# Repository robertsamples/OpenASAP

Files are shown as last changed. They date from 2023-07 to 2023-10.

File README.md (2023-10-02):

# OpenASAP
An Open Source 3D printed Atmospheric Solids Analysis Probe


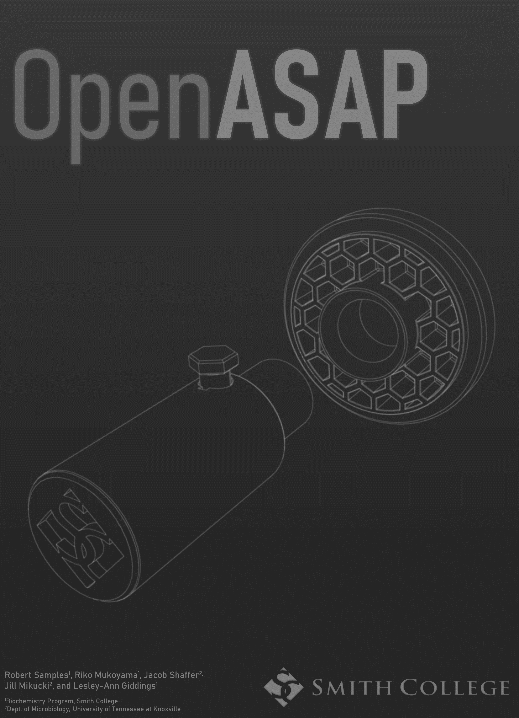
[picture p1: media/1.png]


## Video Tutorial

Click the preview to view the video tutorial and demonstration

[](https://www.youtube.com/watch?v=MM99iZ1kHVs "OpenASAP Tutorial")

## Material selection
### Resin
Any MSLA or SLA resin intended for high temperature applications can be used according to the manufacturer’s instructions. Sirayatech Sculpt Ultra and Formlabs resins have been verified to work. The probe body should be printed in the upright orientation due to the design of the internal structure.

### FDM
An FDM printer may be used with a material with an appropriately high heat deflection temperature such as nylon, polycarbonate, or annealed PLA according to the manufacturer’s instructions. ABS should not be used as depolymerization and release of styrene may cause high MS background, although this has not been proven. Annealed carbon fiber PLA is suggested as the preffered material as it has been proven to withstand the temperatures of the MS inlet for long periods of time, does not release volatile organic compounds in our experience, and is easy to print with an affordable hardened steel nozzle on an unenclosed printer. We suggest use of a 0.4 mm nozzle with standard voron settings (3-4 perimeters, 40% infill) and organic/tree supports inside the button channel.

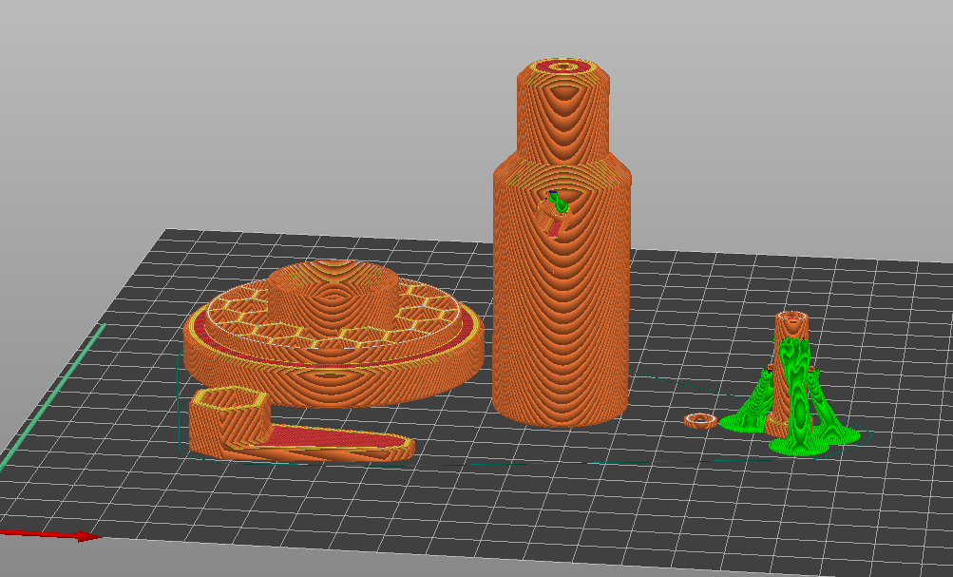
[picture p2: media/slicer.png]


If carbon fiber PLA is selected part annealing may be done in a laboratory oven, however we annealed parts using the printer heat bed. This was done by placing the parts on a 1 cm bed of gyroid infill printed with 3 walls and no top layers to allow airflow, covering the parts with a box made of 1 cm packing foam in which the 3D printer was shipped, and heating the bed to 100 °C for 30 minutes. Parts were allowed to cool slowly to below the glass transition temperature of approximately 50 °C before being removed from the chamber. Corrections for any contraction and expansion of printed parts were done by printing a 20 mm calibration cube and measuring the X, Y, and Z dimensions before and after annealing. A 1% contraction in X and Y dimensions and 2% expansion in Z dimension were found and thus parts were scaled prior to slicing to compensate for these modifications. Scaling requirements may differ depending on material selection and printing parameters.

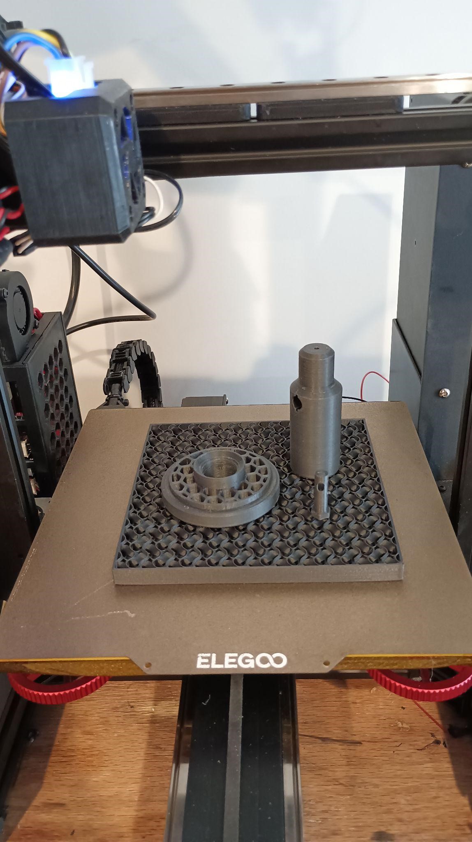
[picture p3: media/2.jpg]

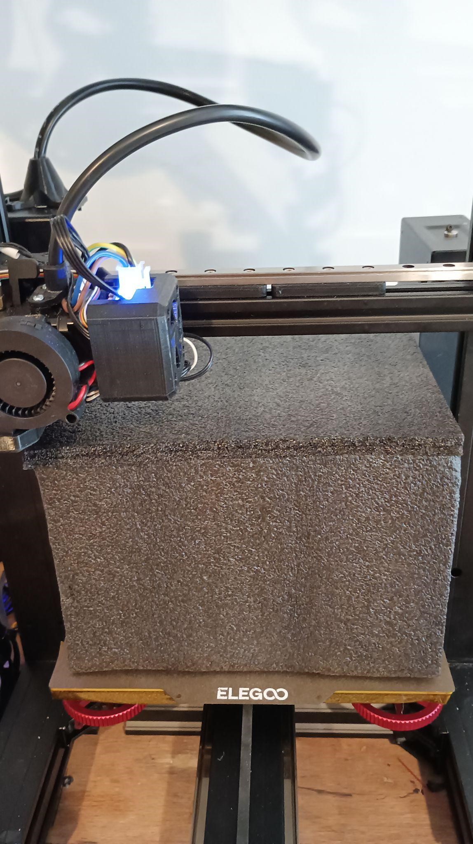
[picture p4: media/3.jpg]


## Postprocessing and assembly

Remove support material if applicable, removal of supports from the inside of the probe channel carefully using forceps or dental picks. Anneal if using carbon fiber PLA, Verify parts fit together properly by inserting the button into the button hole and use the wrench to ensure the button can be turned ¼ turn clockwise to align guide cylinders on the side of the button with the travel channel. Remove the button afterwards

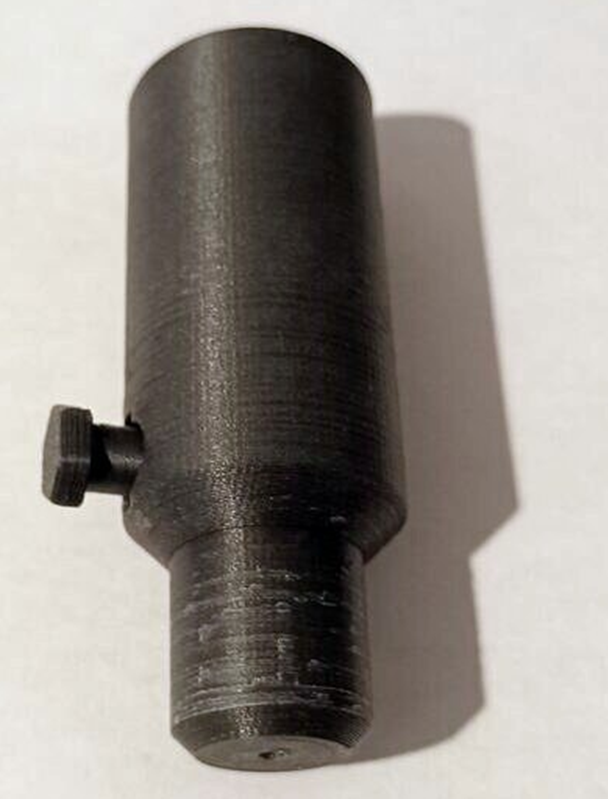
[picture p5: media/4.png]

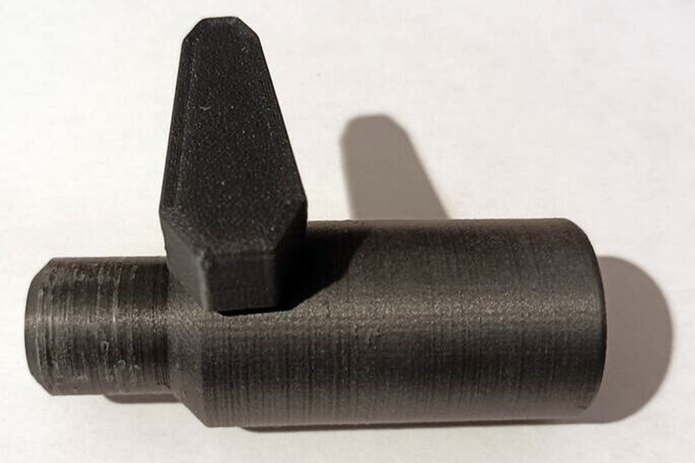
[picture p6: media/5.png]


Disassemble a retractable ballpoint pen or obtain a 4.25 x 18 mm or similar compression spring. The spring shown we used was obtained from a PaperMate InkJoy 300RT pen. The exact dimensions are not critical provided the probe button can reach the depth required to turn into the travel channel. A spring that is longer may be cut to length.

Confirm the spring length, which allows the probe button to be locked into the travel channel. To do this, the spring is placed in the recess of the button and the spring spacer is placed around the spring to prevent it from bending in the button hole. The button is reinserted into the probe as before. If it does not bottom out and turn, try a different pen, or cut the spring to length. Complete the final reassembly of the probe. Although not required,we suggest using a drop of cyanoacrylate glue around the spring spacer and recess in the probe button to secure these to the spring.

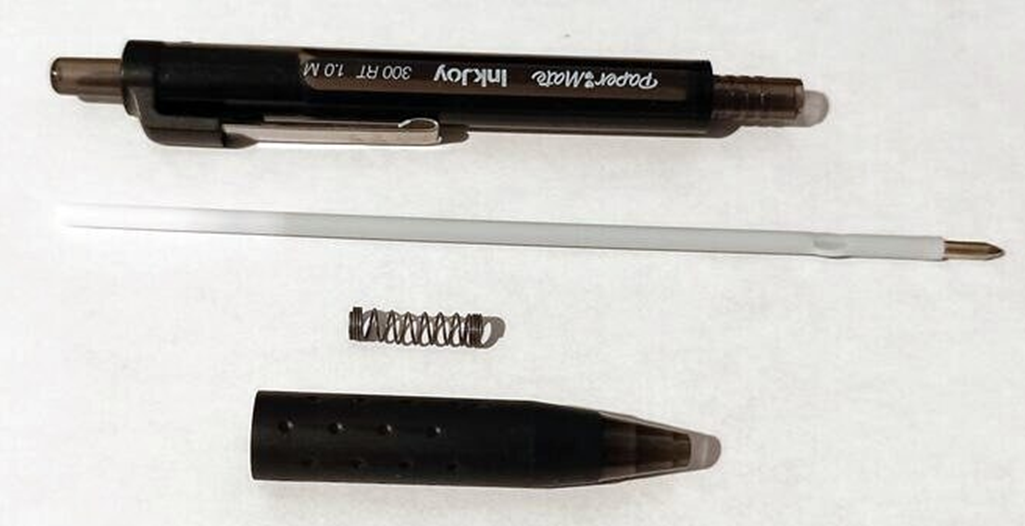
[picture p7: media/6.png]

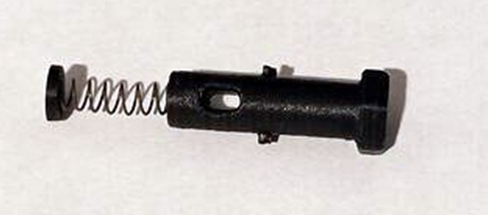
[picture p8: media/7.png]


## Installation

Unscrew the four M2 screws securing the outer housing plate screws on the left side and top of the source housing, as well as the x alignment adjustment nut.



Remove the M4 socket cap screw securing the source housing window side flange.



Remove the flange and replace the acrylic window with printed port, then reassemble flange and housing plates.




Install the IonMax source onto the MS interface and confirm that the tip of the capillary aligns with the MS inlet.


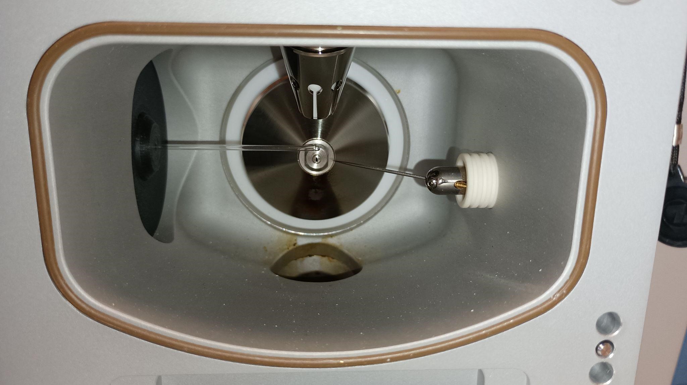
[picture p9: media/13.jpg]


## Use

### Safety
When operating the openASAP system, it is important to avoid contact with heated or electrically charged source components as they can reach high voltages and temperatures. We recommend always putting the mass spectrometer in standby mode when handling the source. Additionally, an electrically insulating material, such as glass, should be used for the sample collecting component of the probe.

### Instrument Configuration
Before using the openASAP system, the APCI source and corona discharge needle must be properly installed in the mass spectrometer housing following the manufacturer's instructions. For Thermo instruments, this involves inserting the APCI source and connecting the LEMO electrical connectors and fittings for auxiliary and sheath gas flow. The corona discharge needle should be inserted into the needle hole and the needle grub screw tightened to secure it. High voltage is supplied through a coaxial LEMO connection on the top of the source housing.

The APCI settings may need to be adjusted based on the analyte and instrument being used. For Thermo instruments, we recommend using the following settings as a starting point: Probe position C, a heater temperature of 325 °C, 5 μA current, and a sheath and auxiliary gas flow rate of 30 and 10 arbitrary units, respectively.

### Sampling

Watch the video (https://github.com/robertsamples/OpenASAP/assets/64489385/52e8197a-4d4a-41fe-b455-a457a1216c5c)

_Video of a 30 second acquisition with a previous vesion of the OpenASAP probe_

To load a capillary into the ASAP probe, depress the button and insert the capillary open end first until it reaches the maximum depth.

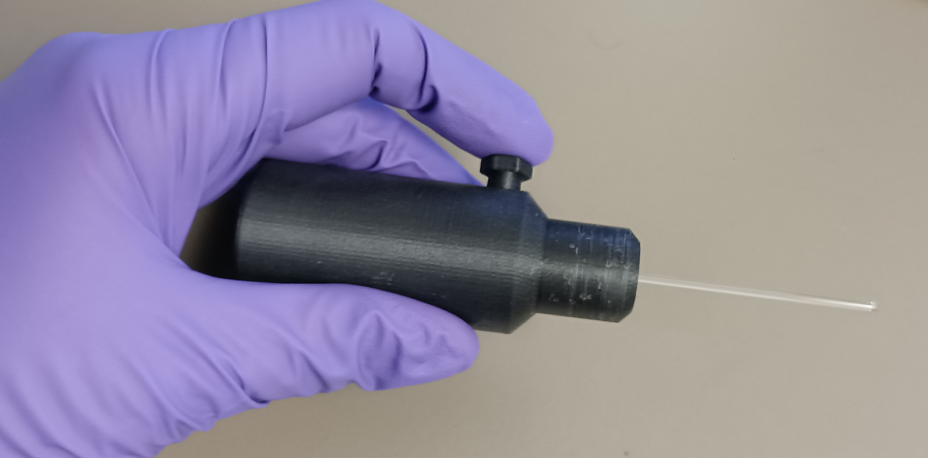
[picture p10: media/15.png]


 Collect the sample on the probe tip and then insert it into the APCI source after starting a continuous or set duration acquisition. 

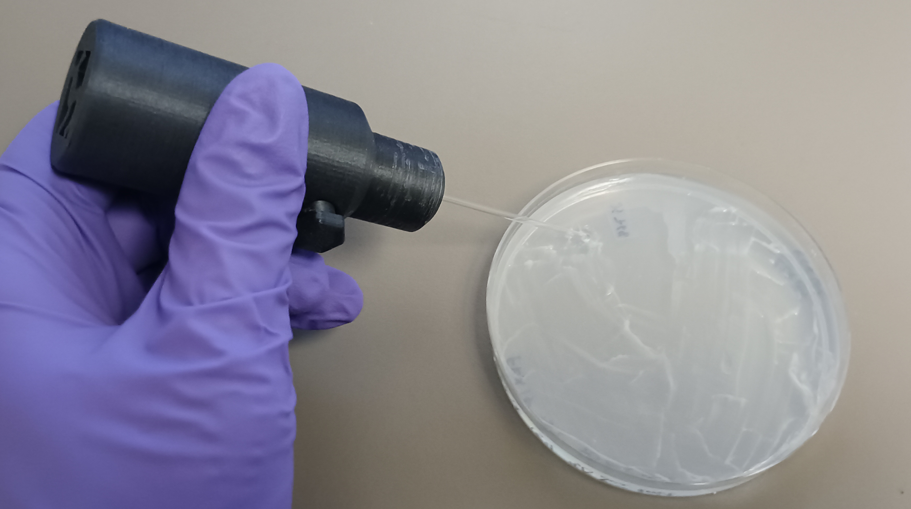
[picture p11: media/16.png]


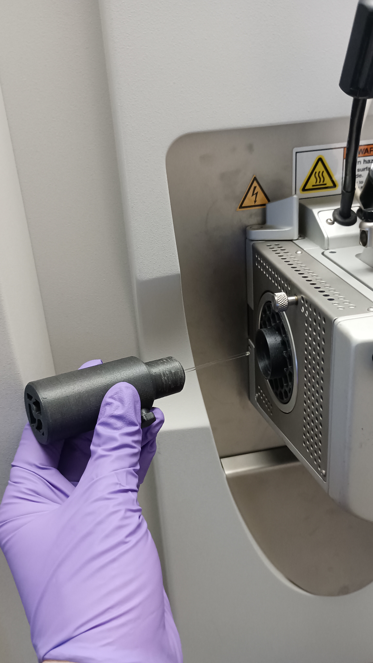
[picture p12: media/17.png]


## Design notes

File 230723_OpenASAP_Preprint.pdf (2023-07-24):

Article title
OpenASAP: an Affordable 3D Printed Atmospheric Solids Analysis Probe (ASAP) Mass Spectrometry System for Direct Analysis of Solid and Liquid Samples

Authors
Robert Samples¹*, Riko Mukoyama¹

, Jacob Shaffer²

, Jill Mikucki²

, and Lesley-Ann Giddings¹ Affiliations

### 1. Biochemistry Program, Smith College, 100 Green St Northampton, MA 01063 2. Department of Microbiology, University of Tennessee at Knoxville, Knoxville, TN 37902

Corresponding author’s email address and Twitter handle
rsamples@smith.edu. @RobertMSamples

### Abstract

Atmospheric Solids Analysis Probe (ASAP) mass spectrometry is a versatile technique allowing direct sampling of solid and liquid samples, but its adoption is limited due to the high cost of commercial ASAP systems. To address this, we present OpenASAP, an open-source ASAP system for mass spectrometers that can be fabricated for under $20 using 3D printing. Our design is readily adaptable to instruments from different manufacturers and can be produced with a variety of additive manufacturing techniques on consumer-grade 3D printers. The probe allows for rapid sampling of solid and liquid samples without sample preparation, making it useful for high throughput screening, investigating spatial localization and function of analytes in biological samples, and incorporating mass spectrometry in teaching. We demonstrate its effectiveness by obtaining mass spectra of three natural product standards at levels as low as 10 ng/ml in liquid samples, and detecting these metabolites in microbial cultures that are difficult to analyze due to complex sample matrices or analyte properties. Furthermore, we demonstrate direct sampling of thin layer chromatography (TLC) spots of these cultures.

### Keywords

Mass Spectrometry, Atmospheric Solids Analysis Probe, Ambient Ionization

### Specifications table

Hardware name | OpenASAP
Subject area | ● Chemistry and biochemistry ● Biological sciences (e.g., microbiology and biochemistry) ● Environmental, planetary and agricultural sciences ● Educational tools and open source alternatives to existing infrastructure
Hardware type | ● Measuring physical properties and in-lab sensors ● Biological sample handling and preparation
Closest commercial analog | Waters ASAP Probe IonSense ASAP System Advion ASAP System

Open source license | GNU General Public License (GPL)
Cost of hardware | $2.50-12.50
Source file repository | http://doi.org/10.5281/zenodo.8173130
OSHWA certification UID | Pending review

### 1. Hardware in context

Mass Spectrometry (MS) has proven to be an indispensable tool in analysis of complex mixtures and trace analytes in the biological and chemical sciences. [1] However, the most commonly used methods of introducing analytes into the mass spectrometer, including gas chromatography (GC-MS), liquid chromatography (LC-MS), and direct injection require time consuming liquid sample preparation. [2] These methods can also introduce nonvolatile salts and detergents that may interfere with sample analysis[3] or be deposited in a gas chromatography column or mass spectrometer. [4] These limitations reduce the utility of MS in situations where rapid sampling of crude materials is desired.

To overcome these limitations, several atmospheric ionization techniques have been developed with varying ranges of applications, analyte coverage, sample preparation requirements, and cost. [5] These ambient ionization methods involve direct sampling and ionization of analytes. [5] One of the simplest atmospheric ionization techniques is the Atmospheric Solids Analysis Probe (ASAP), [6] which is a peripheral device used in MS to allow rapid probe-based sampling of solids and liquids in conjunction with an Atmospheric Pressure Chemical Ionization (APCI) source. ASAP probes typically consist of a handle into which a thermostable and electrically insulating single-use sampling capillary can be inserted.
[7] A small quantity of solid or liquid sample can be collected on the surface of the capillary, which can be inserted into a port in the mass spectrometer source housing that positions the capillary between the mass spectrometer inlet and the APCI source. The position of the capillary enables analytes to be volatilized and ionized by the heated nitrogen plasma emitted by the APCI source. ASAP-MS has performed favorably in published studies comparing it with DART (Direct Analysis in Real Time) and conventional LC-MS methods. [8]

While commercial ASAP systems are available, they are costly and limited to specific instruments. ASAP systems produced by Waters Technology Corporation cost over $10,000[9] and are only available for their instruments.[10] ASAP add-ons produced by IonSense are available $5,000-10,000 for a wider range of instruments. [11] These costs may be challenging to justify for those investigating the technique. To address these issues, we present OpenASAP, an open source ASAP probe for Thermo Scientific instruments that can be manufactured on a wide range of consumer and industrial 3D printers. We have validated the OpenASAP system for detecting a variety of complex natural product standards at concentrations as low as 10 pg/ml. Additionally, we demonstrate the detection of these molecules in unprocessed microbial cultures with complex matrices and show the utility of the OpenASAP system in downstream processing of microbial extracts through direct analysis of thin layer chromatography (TLC) spots of these extracts.

We hope that the OpenASAP system will facilitate adaptation for a wide range of instruments and increase the accessibility of ASAP-MS. By providing a low-cost alternative to commercial ASAP systems, this technology can be utilized by a broader range of researchers, potentially leading to new discoveries and advancements in the field.

### 2. Hardware description

The OpenASAP system builds on the design of published ASAP systems and has similar functionality and sampling time to commercial ASAP devices.[11,12] Existing ASAP systems can be categorized into two designs. The simplest design, used by Advion[13] (Lansing, NY) and IonSense[11] (Saugus, MA) ASAP systems, involves the use of a probe to position a sampling capillary between the MS inlet and APCI source, which facilitates analyte desorption from the capillary by the heated nitrogen plasma stream.[12] The more complex design used by Waters (Milford, MA) ASAP systems involves inserting the probe and sampling capillary into a channel in the APCI source so that the plasma stream flows past the entire sampling surface. While this approach may have benefits, such as ensuring the entire sampling surface is exposed to desorption gas, more homogeneous flow dynamics, and uniform desorption of analytes, it is more technically challenging and cannot be retrofitted to existing APCI sources. Consequently, the OpenASAP probe is placed in a separate port on the MS source housing rather than in the APCI source itself, as in the case of the Waters system

The OpenASAP system is composed of the following three 3D-printed components: a probe port retrofitted to the existing MS source housing, a probe, and a probe button. Additionally, a 4 x 8 mm metal spring is required for capillary tensioning. Sampling is performed using glass melting point capillaries (90 x 1.8 mm). Similar to existing systems, the probe provides an easy consumable handling mechanism. Existing ASAP systems, such as those produced by Advion, commonly employ a capillary handling system reminiscent of a micropipette. Due to the lack of additive manufacturing materials with both the flexibility and thermal resistance necessary for the capillary securing components to be in close proximity to high temperature nitrogen, the OpenASAP probe uses a spring-loaded locking mechanism on the side of the probe. The chamfered capillary hole in the probe ensures easy insertion of capillaries.

The OpenASAP system can be produced with a range of additive manufacturing techniques, prototyping and fabrication was tested with fused deposition modeling (FDM), stereolithography (SLA), masked stereolithography (MSLA) printers ranging from consumer to industrial grade. However, it is preferable to use a high-temperature photopolymer resin or FDM filament, such as polyamide/nylon or polycarbonate. Initial prototyping was performed using PLA+ on a consumer-grade FDM printer. The prototype showed only slight dimensional instability over several hours of testing. Later prototypes were printed in carbon fiber PLA which was purchased for under $27/kg and annealed on the print bed to achieve high heat resistance without deformation. Use of carbon fiber PLA followed by annealing allows the OpenASAP system to be fabricated on any consumer-grade unenclosed FDM printer with a hardened nozzle.

In contrast to commercial systems costing several thousand dollars,[9,11] the OpenASAP system can be fabricated for as little as $2.50 with consumer grade additive manufacturing equipment depending on equipment availability and material choice. It can be retrofitted to any Thermo Scientific (Waltham, MA) mass spectrometer with an IonMax source housing and APCI source and can be adapted to other instruments as well.

- Lowers barrier to entry for probe-based sampling
- Allows rapid analysis of solids and liquids with no sample preparation required
- Adaptable to a wider range of instruments
- Easy to use probe using standard melting point capillaries with button release mechanism
- Under 30 second sampling time

Design files

### 3. Design files summary

Design file name | File type | Open source license | Location of the file
OpenASAP_Io nMax_V1.step | STEP | GNU General Public License (GPL) | https://github.com/robertsamples/OpenASAP
Port.stl | STL | GNU General Public License (GPL) | https://github.com/robertsamples/OpenASAP
Button.stl | STL | GNU General Public License (GPL) | https://github.com/robertsamples/OpenASAP
Probe_body.stl | STL | GNU General Public License (GPL) | https://github.com/robertsamples/OpenASAP
Spacer.stl | STL | GNU General Public License (GPL) | https://github.com/robertsamples/OpenASAP
Wrench.stl | STL | GNU General Public License (GPL) | https://github.com/robertsamples/OpenASAP

3D models of the OpenASAP system parts are available in both STL format for 3D printing and STEP format for modification in CAD software.

Bill of materials

### 4. Bill of materials summary

Designator | Component | Number | Cost per unit -currency | Total cost -currency | Source of materials | Material type
| 4.25x18 mm or similar ballpoint pen compression spring | 1 $0.25- | 1.00 | $0.25-1.00 | | Metal
FDM Material Option | Tinmorry Carbon Fiber PLA | 0.0675 kg | $27 | $1.82 | | Polymer
MSLA Material Option | Siraya Tech Sculpt Ultra or similar high temperature MSLA Resin | 0.07 kg | $75 | $5.25 | | Polymer
SLA Material Option | Formlabs Form 2 Tough 2000 Resin | .075 L | $200 | $15 | | Polymer

We have tested fabrication of the OpenASAP system using FDM, MSLA, and SLA processes and have included the materials and cost for these options, however only one is required. Total cost of fabrication is estimated to be between $2.50 and $16 depending on material choice. If FDM printing with PLA is selected we suggest the use of either polycarbonate, PA/nylon, or annealed PLA (preferably a carbon fiber composite for dimensional stability during annealing) over ABS/ASA, PETG, or unannealed PLA due to the higher heat deflection temperature of the former materials. Thermal depolymerization of ABS/ASA may additionally increase background in MS spectra, although this has not been tested. Carbon Fiber PLA is an excellent option for newcomers to additive manufacturing as it can be printed on any unenclosed entry level FDM printer with a hardened nozzle and can be annealed to achieve high heat resistance. Resin printing with SirayaTech or similar resin will yield parts with PEEK-like properties but requires comparatively expensive equipment and materials.

### 5. Build instructions

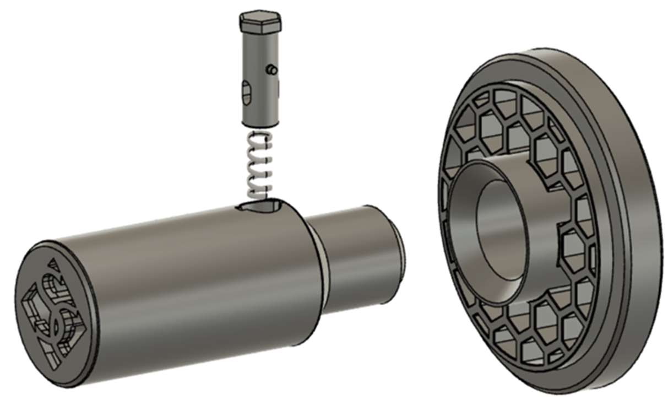
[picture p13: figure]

Figure 1. Exploded Diagram of the Open ASAP probe and port

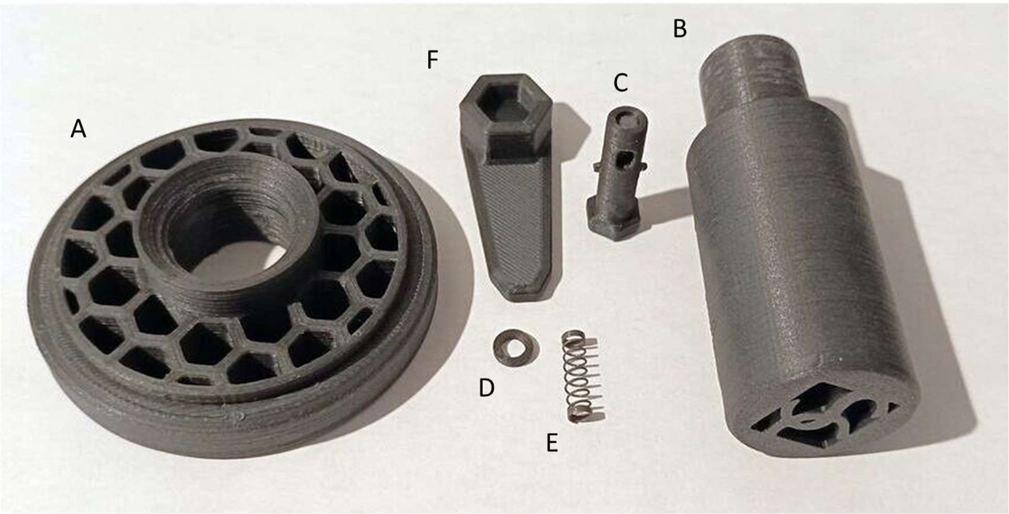
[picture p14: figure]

Figure 2. Image of the parts required for assembly of the probe. A. Probe port B. Probe handle C. Probe button D. Probe spring spacer E. Probe spring F. Probe button wrench

3D Printing

SLA/MSLA
Any resin intended for high temperature applications can be used according to the manufacturer’s instructions. Here Siraya Tech Sculpt Ultra was printed with an Elegoo Mars 3 consumer MSLA printer with an initial resin temperature of 25-30 °C using 50-micron layer height, 2.4 second normal exposure time, 45 second bottom exposure time, and 5 bottom layers. Prints were washed for 10 minutes in 90% isopropanol, immersed in water, and cured under UV light for 10 minutes. SLA printing on a Formlabs Form2 3D Printer was also tested with Formlabs Tough 2000 resin. Appropriate PPE and safety precautions should be adhered to when using any resin printing process due to the toxicity of resins. These include adequate ventilation, use of a secondary enclosure around consumer resin printers to reduce VOC release, and use of an organics respirator when handling resin and uncured parts.

FDM
An FDM printer may be used with a material with an appropriately high heat deflection temperature such as nylon, polycarbonate, or annealed PLA according to the manufacturer’s instructions. Here Tinmorry carbon fiber PLA (ShenZhen Yaduo Trade Co., Ltd, Shenzhen, China) was used on an Elegoo Neptune 3 consumer FDM printer with a 0.4 mm nozzle, 0.2 mm layer height, 4 perimeters, 40% gyroid infill, and automatic organic supports generated by Prusaslicer 2.6 alpha 5 (Prusa Research, Prague, Czech Republic), was used. The parts were annealed for thirty minutes at 100 °C prior to assembly. When sanding carbon fiber PLA or similar composites a respirator must be worn and adequate ventilation used to limit exposure to small carbon fiber particles.

We recommend printing parts in the following orientation when using FDM. Orientation may be changed while using SLA/MSLA although we recommend printing the probe body in the pictured orientation or inverted 180 degrees as the internal geometry has been optimized for printing in these directions.

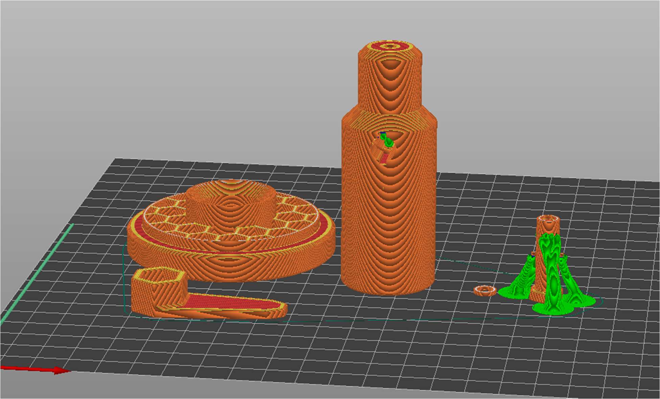
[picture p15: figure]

Figure 3. Example of sliced parts in PrusaSlicer.

Postprocessing and assembly

Remove support material if applicable, removal of supports from the inside of the probe channel carefully using forceps or dental picks. If carbon fiber PLA is selected part annealing may be done in a laboratory oven, however we annealed parts using the printer heat bed. This was done by placing the parts on a 1 cm bed of gyroid infill printed with 3 walls and no top layers to allow airflow, covering the parts with a box made of 1 cm packing foam in which the 3D printer was shipped, and heating the bed to 100 °C for 30 minutes. Parts were allowed to cool slowly to below the glass transition temperature of approximately 50 °C before being removed from the chamber. Corrections for any contraction and expansion of printed parts were done by printing a 20 mm calibration cube and measuring the X, Y, and Z dimensions before and after annealing. A 1% contraction in X and Y dimensions and 2% expansion in Z dimension were found and thus parts were scaled prior to slicing to compensate for these modifications. Scaling requirements may be significantly different depending on material selection and printing parameters.

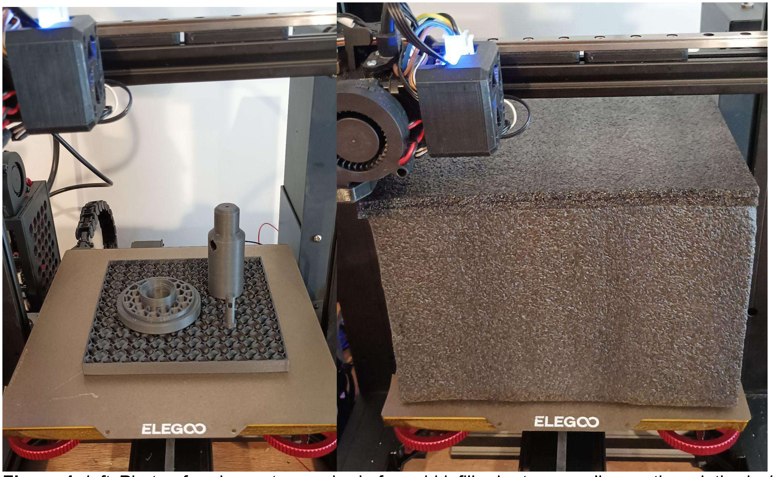
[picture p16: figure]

Figure 4. left. Photo of probe parts on a bed of gyroid infill prior to annealing on the printbed. right. Photo of parts during annealing at 100 °C inside of an insulting box constructed from the foam used to protect the printer during shipping.

Verify parts fit together properly. The button wrench should fit on the top of the button and allow it to be inserted into the button hole.

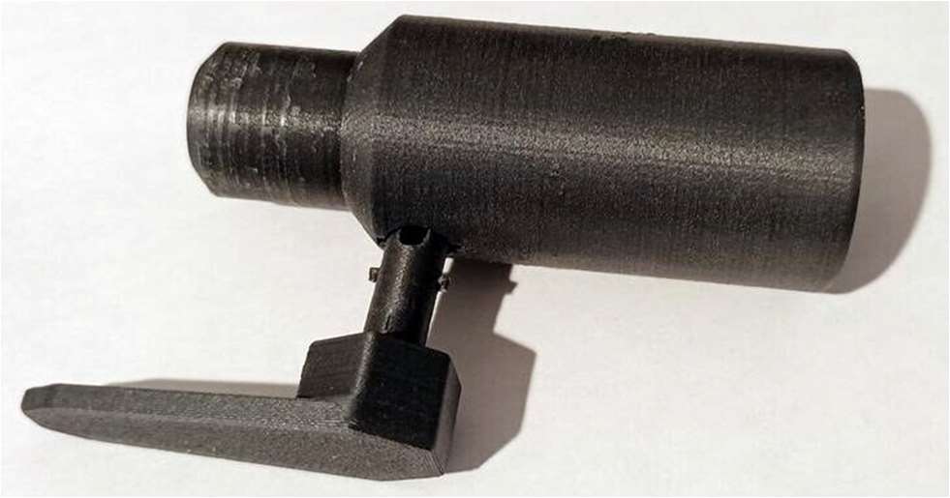
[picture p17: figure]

Figure 5. Photo of the probe button being inserted

When the button bottoms out, it should be turned ¼ turn clockwise to align guide cylinders on the side of the button with the travel channel.

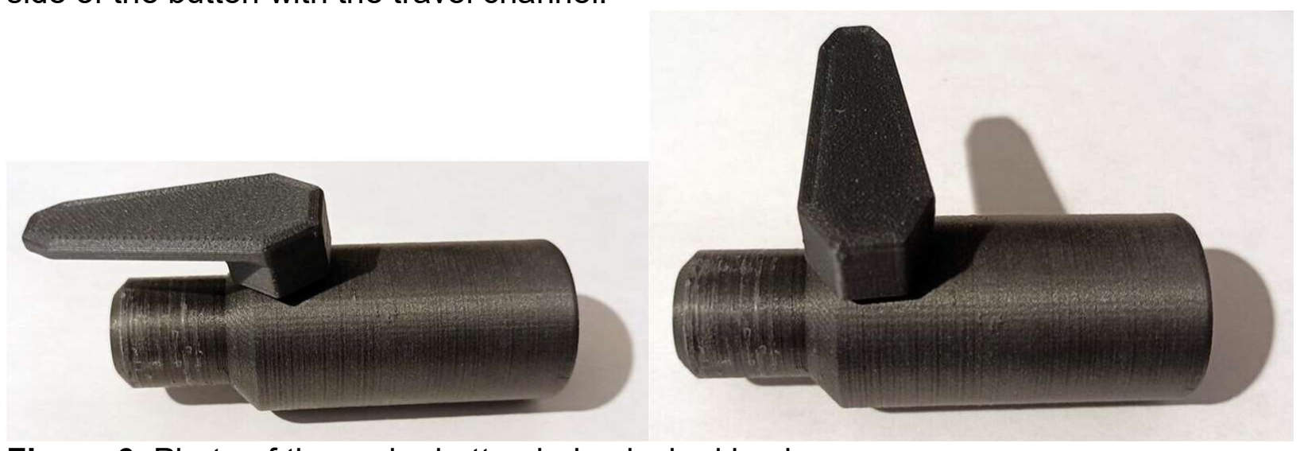
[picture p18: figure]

Figure 6. Photo of the probe button being locked in place.

The button should move freely within the channel. After this is tested, disassemble the button and probe. If parts do not fit together easily confirm all support material has been removed and lightly sand or file if needed. When sanding carbon fiber PLA a respirator is required due to the risks associated with this material.

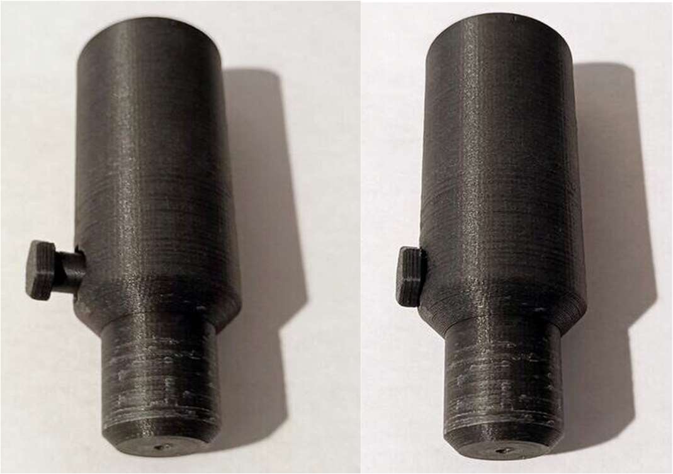
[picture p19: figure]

Figure 7. Photo of the probe with button depressed and extended to check part clearance.

Disassemble a retractable ballpoint pen or obtain a 4.25 x 18 mm or similar compression spring. The spring shown here was obtained from a PaperMate InkJoy 300RT pen. The exact dimensions are not critical provided the probe button can reach the depth required to turn into the travel channel. A spring that is longer may be cut to length.

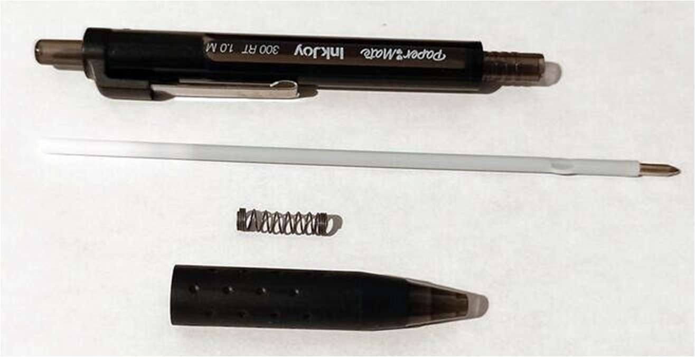
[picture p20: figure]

Figure 8. Disassembled InkJoy 300 RT pen

Confirm the spring length is sufficient to provide tension to the probe button while still allowing the button to be locked into the travel channel. To do this, the spring is placed in the recess of the button and the spring spacer is placed around the spring to prevent it from bending in the button hole. The button is reinserted into the probe as before. If it does not bottom out and turn, try a different pen, or cut the spring to length. Complete the final reassembly of the probe. Although not required, we suggest using a drop of cyanoacrylate glue around the spring spacer and recess in the probe button to secure these to the spring.

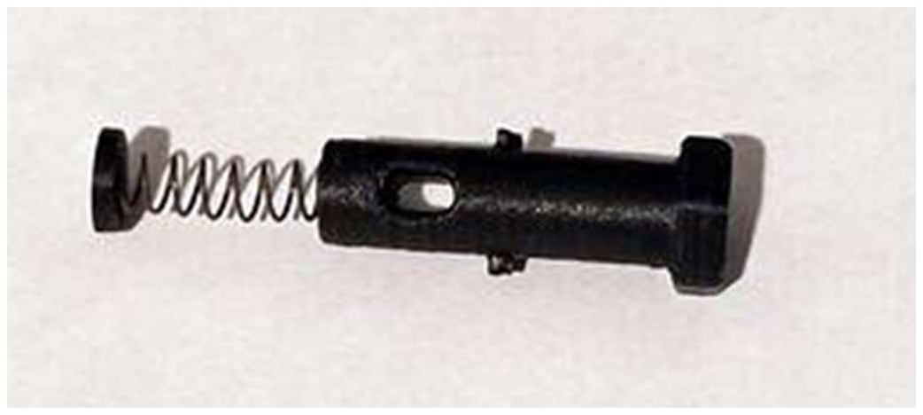
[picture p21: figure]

Figure 9. Probe button, spring, and spacer after before final insertion into the probe body

Unscrew the four M2 screws securing the outer housing plate screws on the left side and top of the source housing, as well as the x alignment adjustment nut. Remove the M4 socket cap screw securing the source housing window side flange.

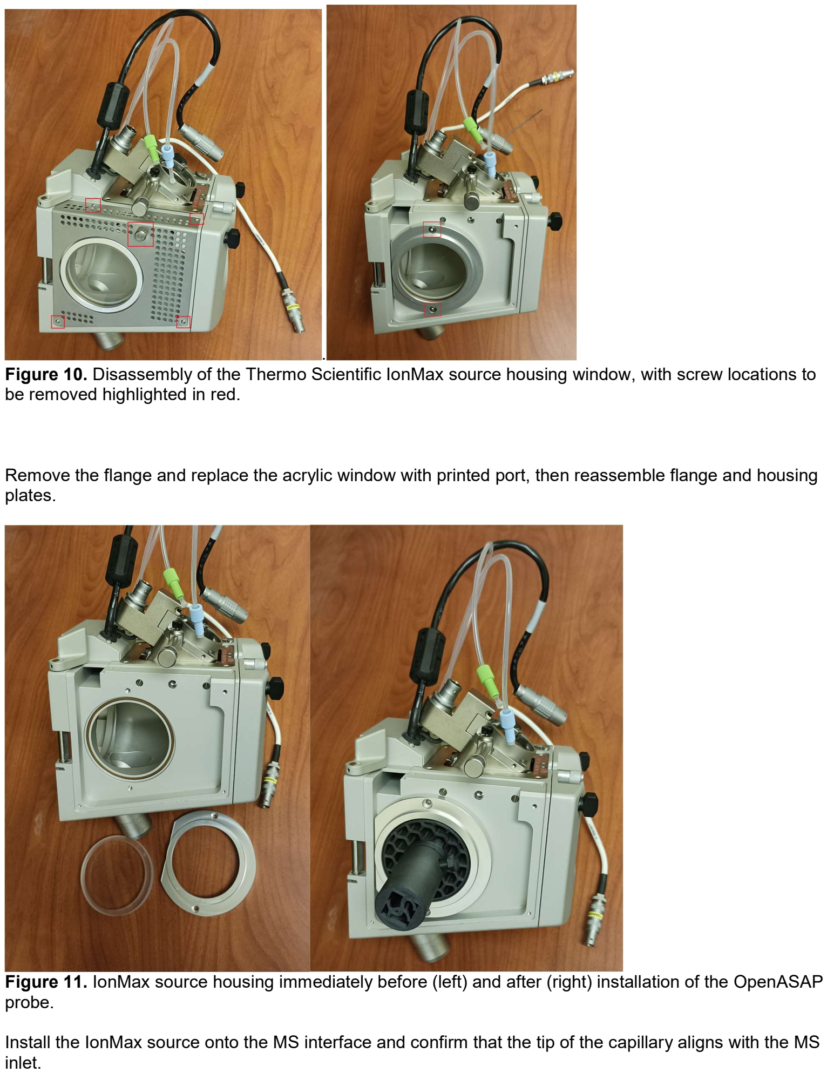
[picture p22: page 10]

Figure 10. Disassembly of the Thermo Scientific IonMax source housing window, with screw locations to be removed highlighted in red.

Remove the flange and replace the acrylic window with printed port, then reassemble flange and housing plates.

Figure 11. IonMax source housing immediately before (left) and after (right) installation of the OpenASAP probe.

Install the IonMax source onto the MS interface and confirm that the tip of the capillary aligns with the MS inlet.

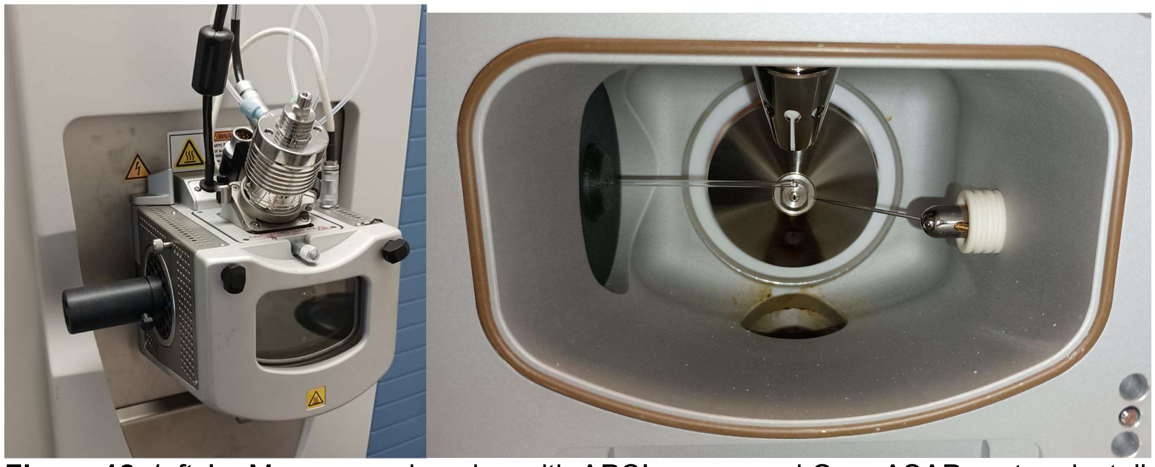
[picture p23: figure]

Figure 12. left. IonMax source housing with APCI source and OpenASAP system installed and mounted on the Q Exactive HF-X. right. View of the MS inlet and source components showing the capillary in the OpenASAP system positioned between the APCI source and MS inlet.

### 6. Operation instructions

When operating the openASAP system, it is important to avoid contact with heated or electrically charged source components as they can reach high voltages and temperatures. We recommend always putting the mass spectrometer in standby mode when handling the source. Additionally, an electrically insulating material, such as glass, should be used for the sample collecting component of the probe.

Before using the openASAP system, the APCI source and corona discharge needle must be properly installed in the mass spectrometer housing following the manufacturer's instructions. For Thermo instruments, this involves inserting the APCI source and connecting the LEMO electrical connectors and fittings for auxiliary and sheath gas flow. The corona discharge needle should be inserted into the needle hole and the needle grub screw tightened to secure it. High voltage is supplied through a coaxial LEMO connection on the top of the source housing.

The APCI settings may need to be adjusted based on the analyte and instrument being used. For Thermo instruments, we recommend using the following settings as a starting point: Probe position C, a heater temperature of 325 °C, 5 μA current, and a sheath and auxiliary gas flow rate of 30 and 10 arbitrary units, respectively.

To load a capillary into the ASAP probe, depress the button and insert the capillary open end first until it reaches the maximum depth.

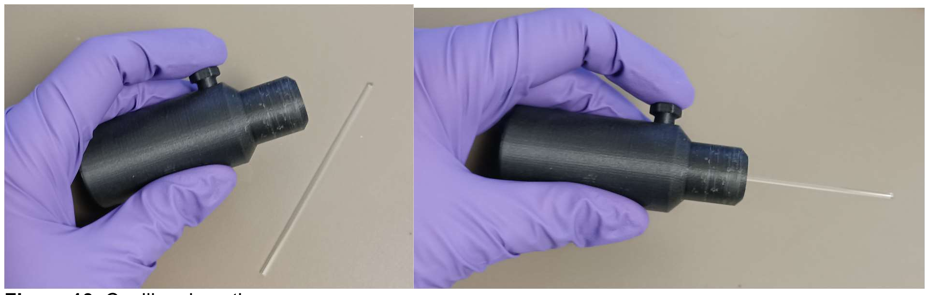
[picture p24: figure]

Figure 13. Capillary insertion process

Collect the sample on the probe tip and then insert it into the APCI source after starting a continuous or set duration acquisition.

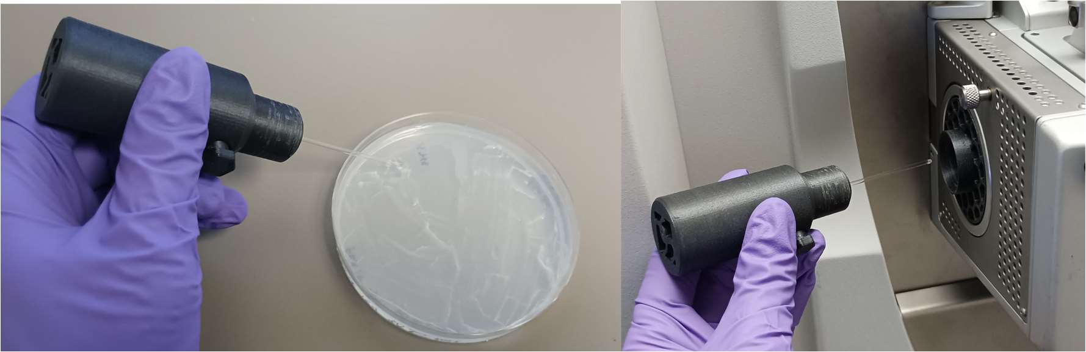
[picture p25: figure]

Figure 14. left. Direct sampling of Arthrobacter sp. strain FRX14 on agar right. insertion of the probe following sampling

Observe the mass spectra as they are acquired. When the signal intensity diminishes as analytes are desorbed from the probe, end the acquisition and withdraw the probe from the source housing. Depress the button over a glass waste container to dispose of the capillary. In some cases where volatile analytes are completely desorbed by the nitrogen stream, the capillary may be reusable.

### 7. Validation and characterization

Data Collection

Three microbial strains possessing biosynthetic gene clusters for the production of secondary metabolites with a range of different polarities and molecular weights were selected for validation studies. These included two Antarctic microbial strains, M. frigida DJPM01 and Arthrobacter sp. strain FRX14, which possess prodigiosin and ectoine gene clusters, respectively.[14] Prodigiosin is a basic and highly aromatized compound, [15] tetracycline is a moderately polar polyketide synthase product, [16] and ectoine is small zwitterionic and highly polar compound for which we have been unable to achieve acceptable retention with C18 columns (Fig. 20). Additionally, Streptomyces alboflavus (NRRL B-1273), a known tetracycline producer,[17] was included. These strains were cultured for two weeks on solid media. Streptomyces alboflavus (NRRL B-1273) was cultured on ISP2 agar plates and incubated at 28 °C while the Antarctic strains were cultured on R2A (BD Difco, Franklin Lakes, NJ) agar plates at 4 °C. Diffusible yellow pigment was evident in Streptomyces alboflavus (NRRL B-1273) plates and non-diffusible red pigment was noted in Massilia frigida DJPM01 plates.

Analytic standards of prodigiosin, ectoine, and tetracycline were purchased (Sigma-Aldrich; St. Louis, MO) and standard solutions standard solutions ranging from 1 x 10⁻² - 10⁻¹⁴ g/mL were generated in 10-fold dilutions, 1 x 10⁻² and 1 x 10⁻³ g/ml concentrations were excluded for prodigiosin. To determine the approximate limit of detection for these analytes the ASAP capillary was inserted into 900 µl of each standard in a microcentrifuge tube and inserted into the probe port while data was acquired with the source parameters listed in the operation section, a SIM scan range from the exact mass of the M+H ion of the standard ± 2.5 Da, 30,000 resolution, 1e6 AGC target, and 50 ms max injection time. Extracted ion chromatograms for the precursor ion were generated in Thermo Scientific Freestyle and the peak in the chromatogram view was integrated to determine the quantity of standard detectable at each concentration and to generate a standard curve.

ASAP identification of these compounds microbial cultures were acquired by touching the probe the surface of a colony and inserting into the port as before with a SIM method. Sampling of the prodigiosin producer M. frigida DJPM01 was conducted in full scan mode with a 50-750 Da scan range as prodigiosin’s m/z 324 for the [M+H] adduct was the base peak. After desorption was complete, a standard of a known concentration was collected on a new capillary and inserted to provide a reference within the same raw acquisition file. The experiment was repeated to acquire full scan MS spectra with a 50-750 Da scan range and MS/MS data with a 0.9 Da isolation window, 35 V NCE, and MS/MS mass range of 50-750.These data were visualized in Thermo Freestyle. Extracted ion chromatograms for the targeted precursor masses were generated to view the quantity of analyte detected during insertion of the probe with microbial samples and standards.

To determine the volume of sample retained on the capillary we use a spectrophotometer to measure the absorbance of the tetracycline standard curve, sampled a 10 mg/ml solution, dispersed this material in 1 ml methanol, and measured the absorbance of the resulting solution. The tetracycline concentration of this solution was used to calculate the dilution factor from the sampled stock and thus the volume added.

To evaluate the OpenASAP system in downstream processing of samples or reaction mixtures and in screening, TLC was run on ethyl acetate extracts of M. frigida DJPM01 grown for 10 days on R2A media at 4 °C used in a previous study. [14] The ethyl acetate extract of M. frigida DJPM01 and prodigiosin were separately spotted on TLC plates, (10x10 cm aluminum backed 60 mesh F254 silica plates, Beijing Laikensi Technology Development Co. Ltd., Beijing, China) which were run with a 90:10:1 chloroform:methanol:formic acid mobile phase. The open end of the melting point capillaries was used in the openASAP probe to scrape a small quantity of selected TLC spots and MS data was acquired as previously described with a full scan method (50-750 Da). Depending on the consistency of the stationary phase, spraying the plate with a small quantity of solvent or water prior to scraping may help. Previous work has used a similar procedure in which the TLC plate is scraped and a wetted probe dipped in the stationary phase.[18]

Results and Discussion

The 3D printed atmospheric analysis sampling probe (ASAP) peripheral was successfully integrated with a mass spectrometer to directly detect three microbially produced small molecule natural products, ectoine, prodigiosin, and tetracycline. Without requiring large quantities of microbial cultures and sample preparation, metabolites were directly detected in solids (i.e., TLC and agar plates) and liquids. The high flexibility and sensitivity of this technique is especially notable in light of the low cost of the OpenASAP system. Ectoine (143.0818 m/z, 1.76 ppm error), prodigiosin (324.2072 m/z, 1.19 ppm error), and tetracycline (445.1620 m/z, 2.04 ppm error) were successfully identified in Arthrobacter sp. strain FRX14, M. frigida DJPM01, and Streptomyces alboflavus (NRRL B-1273), respectively. (Figs. 15-
17) In addition, the MS/MS spectra obtained for all three compounds in the microbial strains were consistent with the fragmentation patterns obtained from the standards. (Figs. 15-17)

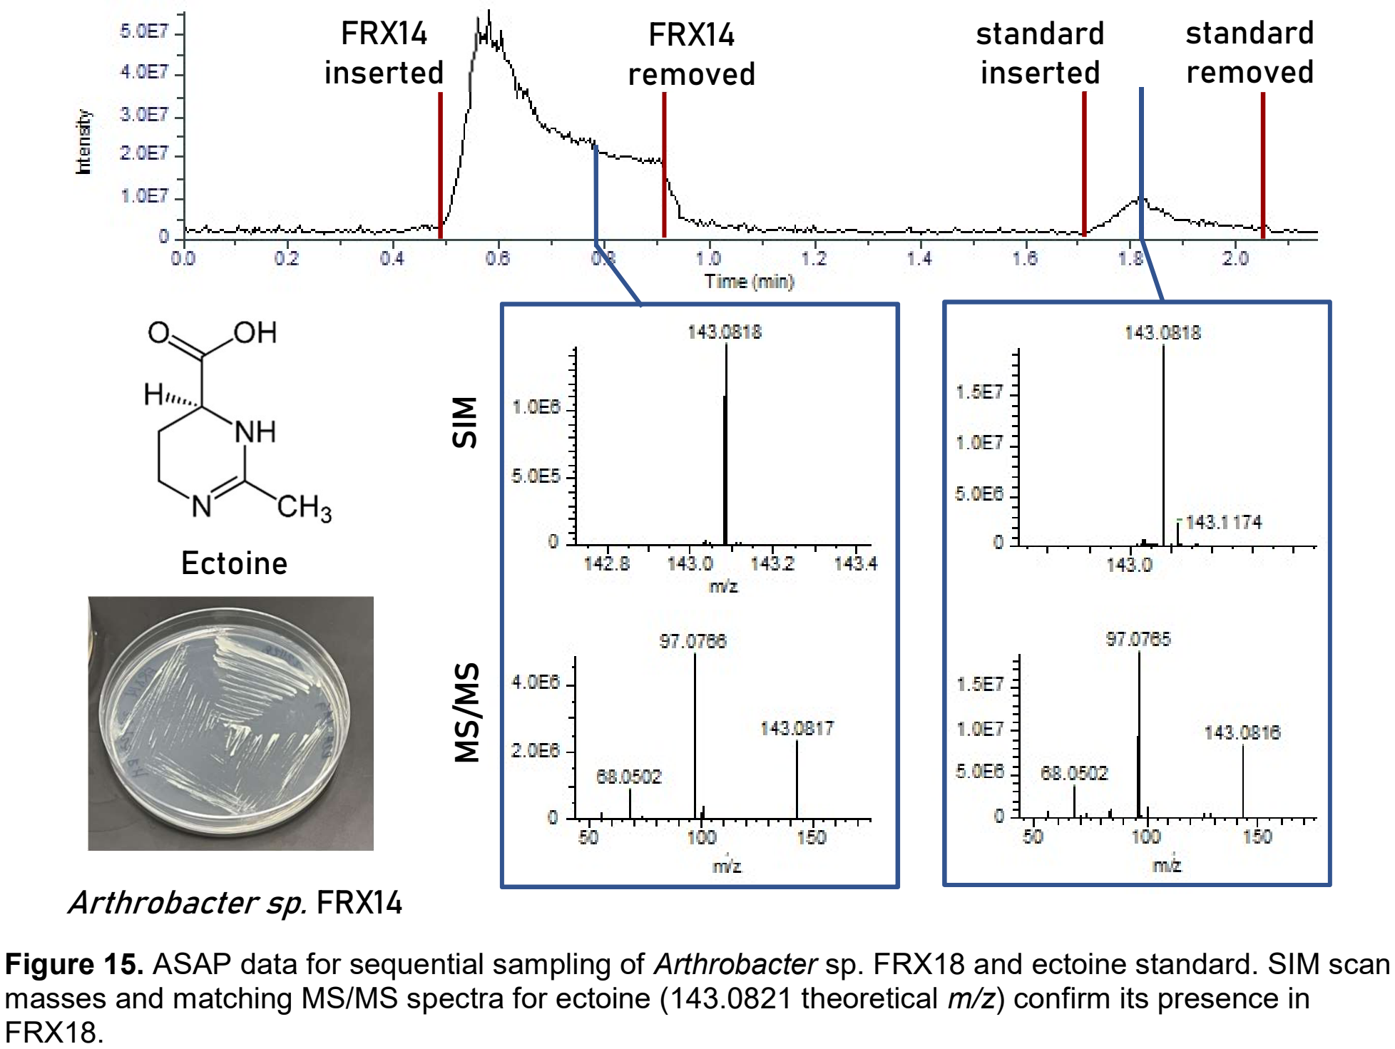
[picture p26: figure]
FRX18.; SIM MS/MS; FRX14 inserted; FRX14 removed; standard inserted; standard removed; Arthrobacter sp. FRX14; Ectoine

Figure 15. ASAP data for sequential sampling of Arthrobacter sp. FRX18 and ectoine standard. SIM scan masses and matching MS/MS spectra for ectoine (143.0821 theoretical m/z) confirm its presence in

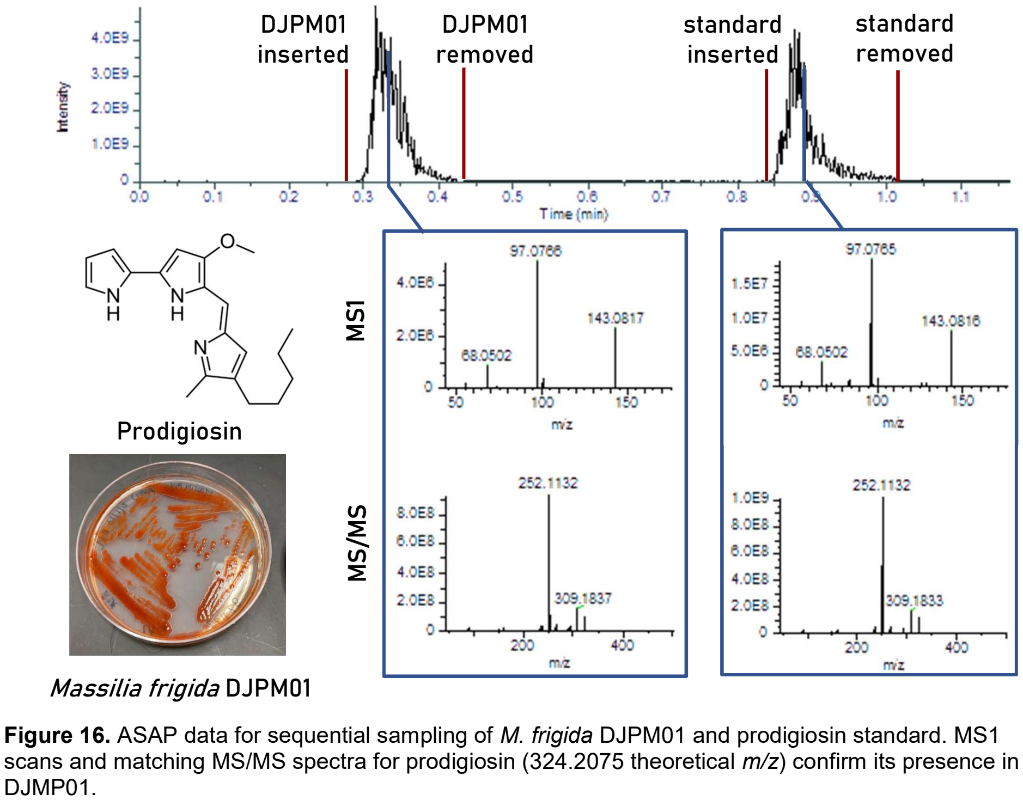
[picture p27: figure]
DJMP01.; MS¹ MS/MS; DJPM01 inserted; DJPM01 removed; standard inserted; standard removed; Massilia frigida DJPM01; Prodigiosin

Figure 16. ASAP data for sequential sampling of M. frigida DJPM01 and prodigiosin standard. MS1 scans and matching MS/MS spectra for prodigiosin (324.2075 theoretical m/z) confirm its presence in

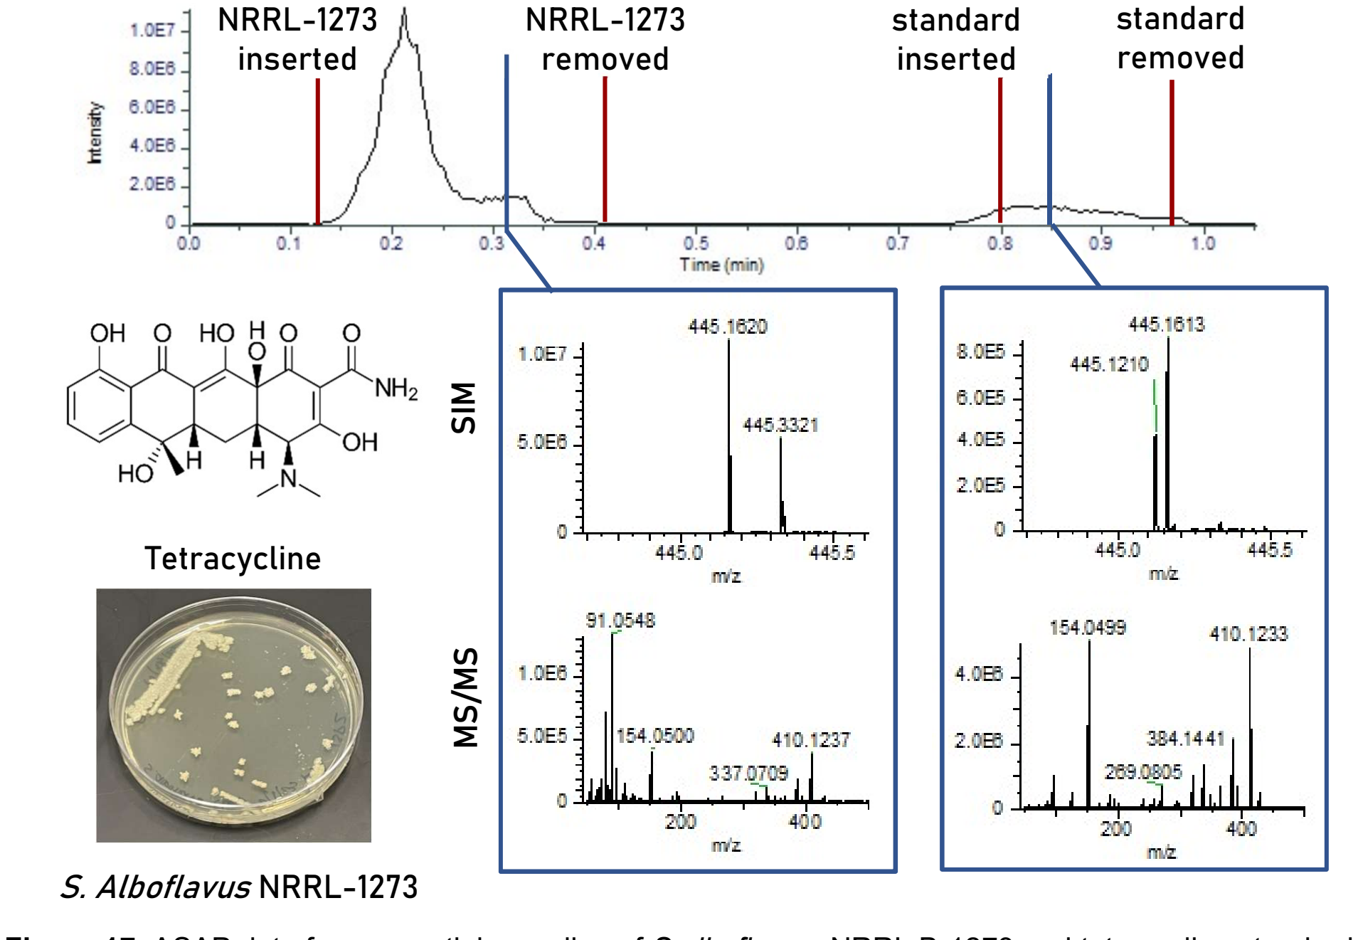
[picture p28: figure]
NRRL-1273 inserted; NRRL-1273 removed; standard inserted; standard removed; S. Alboflavus NRRL-1273; Tetracycline

Figure 17. ASAP data for sequential sampling of S alboflavus. NRRL B-1273 and tetracycline standard. SIM scan masses and the presence of numerous key fragments MS/MS spectra for tetracycline (445.161093 theoretical m/z) confirm its presence in S. alboflavus NRRL B-1273. Additional fragments are present in the MS/MS spectra and these are likely due to the presence of isobaric compounds. Use of a multiple reaction monitoring method may be desirable in such cases.

Sensitivity and analyte specific behavior

Sensitivity varied significantly for each compound, with an approximate limit of detention for ectoine being 10 pg/ml, prodigiosin at 10 ng/ml, and tetracycline at 100 ng/ml. Within the range of linear detector response R²

was found to be between 0.958 and 0.997 for the compounds tested (Fig. 18). The sensitivity correlated with volatility and inversely correlated with molecular weight, which was unsurprising given our use of an atmospheric pressure chemical ionization (APCI) ionization source. We found that the sampling volume was approximately 7.3 µl. (Fig. 19) which places the absolute limit of detection at 7 fg for ectoine, 7 pg for prodigiosin, and 70 pg for tetracycline. SIM MS/MS

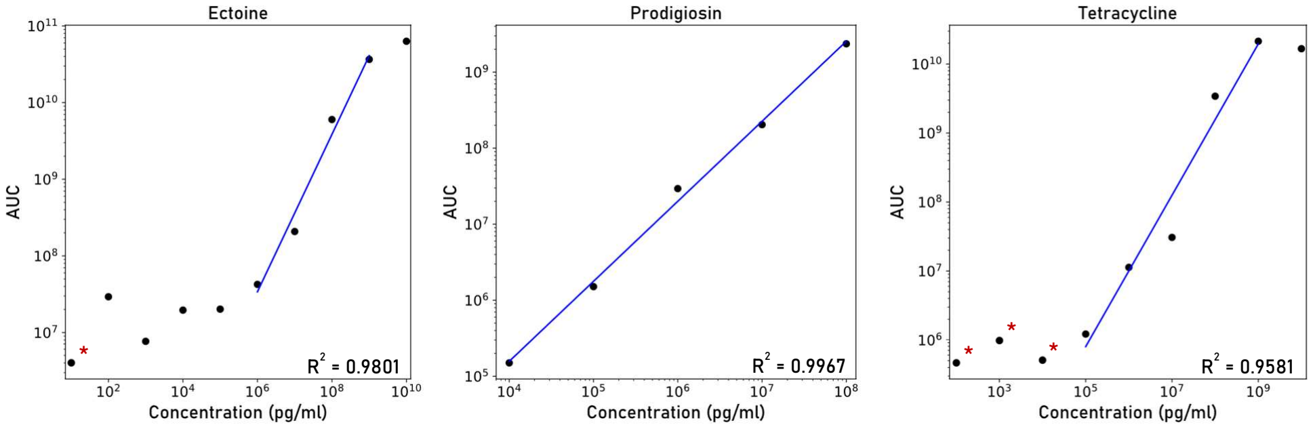
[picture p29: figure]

Figure 18. Standard curves for the natural product standards tested. Data points marked with red asterisks were below the limit of detection (S/N 10 threshold).

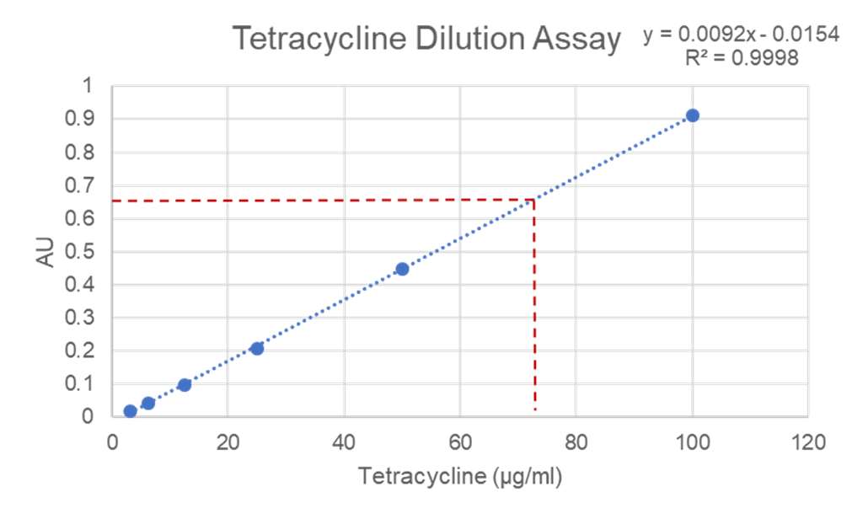
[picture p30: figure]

Figure 19. Standard curve of tetracycline solutions based on absorbances with the red lines denoting the absorbance and concentration of a 10 mg/ml solution of tetracycline sampled with the OpenASAP system, and then dispersed into 1 ml methanol. The final concentration of 73 μg/ml indicates a sampled volume of 7.3 μl.

During heating of high concentration tetracycline standards by the APCI source, formation of pyrrolized material was noted. Similarly, we found that ASAP is not suitable for peptidic analytes such as desferrioxamine, which was observed to completely degrade (data not shown). Despite the observed pyrolysis of tetracycline at high concentrations the limit of detection is similar to that previously reported for quantitation of tetracycline on the QE HF-X in a traditional LC-MS workflow (20 ng/g in samples after extraction and concentration, the next concentration below 100 ng/ml used in this study was 10 ng/ml).[19]

By contrast, ectoine is very challenging to detect in environmental samples with LC-MS using conventional C18 stationary phases due to its high polarity (Fig. 20), but very easy using ASAP. The high polarity of ectoine is particularly problematic for samples that contain nonvolatile salts as ectoine may be lost during desalting with SPE cartridges, and the use of a divert valve to protect the mass spectrometer will also divert ectoine. (Fig. 20) In cases where analysis with a HILIC column is not possible or desirable, ASAP may be an attractive alternative. We observed a very large difference between the limits of detection (based on the presence of an integrable peak and S/N>10) and quantitation (based on the region of linearity). It is unclear why this behavior occurs. Adsorption of analytes to HPLC vials is a well-known confounder in trace analyte analysis[20] and it is conceivable that a similar phenomenon occurs in which analytes are adsorbed and concentrated on the capillary until saturation of surface sites occurs at approximately 100 ng/ml for ectoine. If this is the case the effect may be advantageous for some applications however it should not be relied upon as adsorption may be matrix dependent.

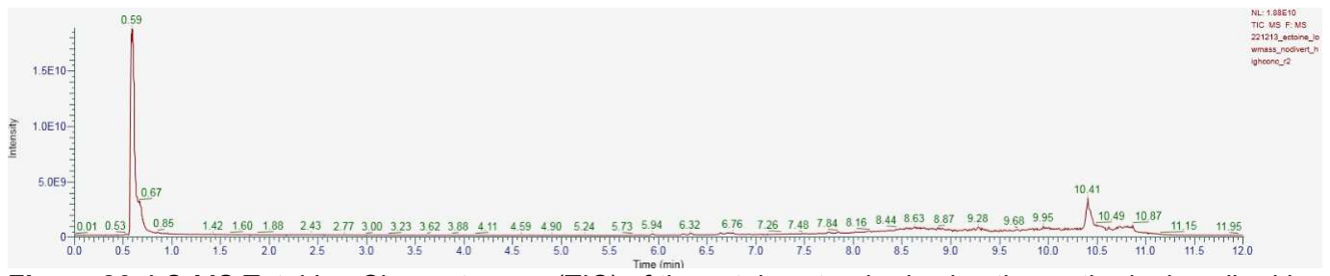
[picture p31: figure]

Figure 20. LC-MS Total Ion Chromatogram (TIC) of the ectoine standard using the methods described in Shafter et al. (2023) [14]. Ectoine elutes within the solvent front at 0.59 minutes due to its high polarity. Analysis of microbial cultures like those used in this study would not be possible as a divert valve would need to be employed to divert salts in the solvent from contaminating the mass spectrometer.

The limits of detection and quantitation for prodigiosin appear to be similar as no integrable peak was present under 10 ng/ml and the detector response was linear over the entire concentration range tested with R²>0.99. Interpretation of ASAP data may be complicated as no orthogonal separation method is employed, as such spectra can be complex. Thus, it may be more appropriately used in targeted workflows where standards are available. Prodigiosin was a notable exception to this as in both the standard and microbial sample it (m/z 324.2072) was the base peak in MS1 spectra and thus we presented MS1 spectra obtained with a full scan method in Fig. 16. The mass of the prodigiosin analogue 2-methyl-3-butyl prodiginine (m/z 310.1915) is conspicuous in these spectra and we have previously documented the production of this compound by M. frigida DJPM01.[14]

TLC-MS with OpenASAP

TLC analysis (Fig. 21) revealed the presence of two red pigmented compounds, identified as prodigiosin (324.2076 m/z, Rf 0.8) and another compound we have yet to conclusively identify (Rf 0.71), in the ethyl acetate extract of M. frigida DJPM01. Two other orange pigmented compounds were observed which likely represent short-lived decomposition intermediates as one was observed in the authentic standard. These proved very unstable on silica and likely in storage as they could not be observed when TLC was repeated. The Rf value of prodigiosin present in the microbial extract was identical to that of an authentic standard. Work to refine TLC plate sampling is ongoing.

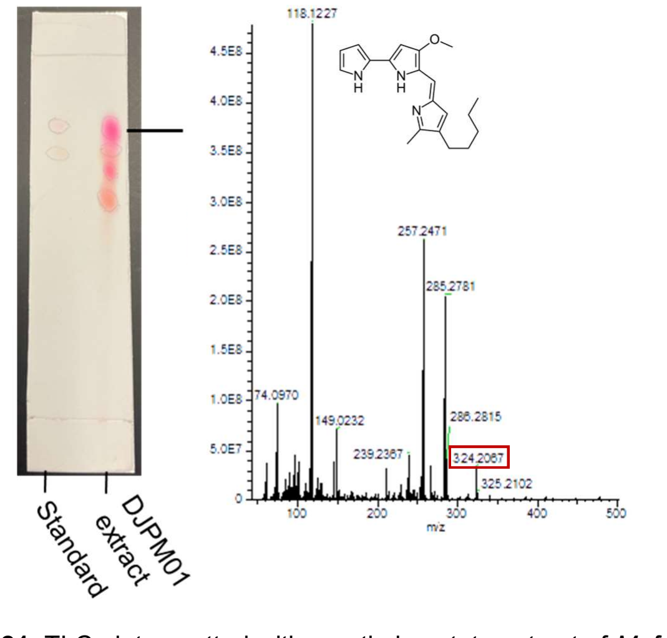
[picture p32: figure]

Figure 21. TLC plate spotted with an ethyl acetate extract of M. frigida DJPM01 and prodigiosin standard, and the corresponding MS1 spectra obtained from conducting ASAP on the prodigiosin spot.

OpenASAP Applications and Future Directions

3D printers are now common shared resources at academic institutions, enabling this technology to be more accessible. However, if such resources are not available, the system can be printed on even very low-cost consumer grade 3D printers with the addition of an affordable hardened steel nozzle. We estimate that an investigator with no tools or consumables could reasonably purchase these and fabricate the system for under $200.

ASAP can facilitate the detection of compounds in complex sample matrices that are undetected by traditional ionization methods. As evidenced by our detection of ectoine, which was not tractable using conventional LC-MS methods, the flexibility and high sensitivity of ASAP is desirable for its detection. This can be beneficial for analytical analyses of extreme environments, which are subject to extreme ranges of chemical and physical variables, including hypersaline ponds, metal contaminated sites, or locations with extreme pH.[21–23] These locales are considered to be edge cases in terms analytical chemistry, where analytical methods may be more challenging or less thoroughly validated,[21–23] and ASAP is useful for these applications as no specialized LC or sample preparation methods need to be employed.

ASAP has the potential to accelerate or enhance other techniques. The use of the OpenASAP system coupled with TLC to detect prodigiosin and another closely eluting compound in the ethyl acetate extract of M. frigida DJPM01 demonstrates the potential of this system for downstream processing of complex mixtures. TLC remains a widely used technique for separation of complex mixtures,[24] and the ability of OpenASAP to detect compounds of interest directly from the TLC plate can greatly expedite screening and analysis of these mixtures. Furthermore, the use of OpenASAP in bioassay-guided fractionation of natural products may be highly beneficial, particularly in conjunction with bioautography as bioactive TLC spots on a plate could be directly sampled to assign putative identifications during dereplication of known compounds. Similarly, the system can be used for screening of synthetic reaction products, where it can quickly identify the presence and purity of target compounds, eliminating the need for time-consuming purification steps.

While ASAP has many advantages, researchers should be cognizant of the low stability of some compound classes in APCI ionization conditions. Future studies could adapt ASAP to ionization sources more appropriate for larger compounds or those with poor thermal stability, such as desorption electrospray ionization (DESI), [25] dielectric barrier discharge ionization (DBDI), [26] or low temperature plasma ionization (LTP). [27]

Conclusions

The OpenASAP system increases the accessibility of affordable, ambient ionization and sampling techniques to researchers. While we have validated this system to detect low-abundance secondary metabolites in microbial cultures, OpenASAP can be employed in many other applications as ASAP and other ambient ionization techniques, such as DART, have been used in diagnostic medicine, forensic science, chemical ecology, and for environmental monitoring. The lack of solvents and noble gasses required for operation make the OpenASAP system an attractive option for mass spectrometry in remote locations where resources are limited. Future studies could further optimize the OpenASAP system for different applications and investigate its potential use in field testing, where a small linear ion trap instrument, a portable nitrogen concentrator, and an ASAP system could be utilized. Overall, the OpenASAP system presents a promising platform for the rapid and sensitive detection of a wide range of analytes in various fields.

### CRediT author statement

Robert Samples: Conceptualization, Methodology, Visualization, and Investigation, Writing- Original draft preparation. Riko Mukoyama: Investigation Jacob Shaffer: Resources and writing. Jill Mikucki: Resources, writing, funding acquisition. Lesley-Ann Giddings: Investigation, Writing- Original draft preparation, funding acquisition .

### Acknowledgments

We are grateful for the assistance of Eric Jensen, Director of the Center for Design and Fabrication at Smith College, for assistance with fabrication of the ASAP probe.

Funding: This work was supported by the National Science Foundation Office of Polar Programs [ #2148730 to JAM and #2148731 to L-AG].

### References:

[1] C. Li, S. Chu, S. Tan, X. Yin, Y. Jiang, X. Dai, X. Gong, X. Fang, D. Tian, Towards Higher Sensitivity of Mass Spectrometry: A Perspective From the Mass Analyzers, Front. Chem. 9 (2021). https://www.frontiersin.org/articles/10.3389/fchem.2021.813359 (accessed July 14, 2023).
[2] R.M. Smith, Before the injection—modern methods of sample preparation for separation techniques, J. Chromatogr. A. 1000 (2003) 3–27. https://doi.org/10.1016/S0021-9673(03)00511-9.
[3] B. Cañas, C. Piñeiro, E. Calvo, D. López-Ferrer, J.M. Gallardo, Trends in sample preparation for classical and second generation proteomics, J. Chromatogr. A. 1153 (2007) 235–258. https://doi.org/10.1016/j.chroma.2007.01.045.
[4] T.M. Annesley, Ion Suppression in Mass Spectrometry, Clin. Chem. 49 (2003) 1041–1044. https://doi.org/10.1373/49.7.1041.
[5] T.-H. Kuo, E.P. Dutkiewicz, J. Pei, C.-C. Hsu, Ambient Ionization Mass Spectrometry Today and Tomorrow: Embracing Challenges and Opportunities, Anal. Chem. 92 (2020) 2353–2363. https://doi.org/10.1021/acs.analchem.9b05454.

[6] E.A. Bruns, V. Perraud, J. Greaves, B.J. Finlayson-Pitts, Atmospheric Solids Analysis Probe Mass Spectrometry: A New Approach for Airborne Particle Analysis, Anal. Chem. 82 (2010) 5922–5927. https://doi.org/10.1021/ac101028j.
[7] Library Details | Waters. https://www.waters.com/nextgen/us/en/library/library-
details.html?documentid=720003907&t=waters-ASAPApplicationNotebook-720003907 (accessed July 14, 2023).
[8] J. Osorio, M. Aznar, C. Nerín, C. Elliott, O. Chevallier, Comparison of LC-ESI, DART, and ASAP for the analysis of oligomers migration from biopolymer food packaging materials in food (simulants), Anal. Bioanal. Chem. 414 (2022) 1335–1345. https://doi.org/10.1007/s00216-021-03755-0.
[9] Contractor Information Summary - New York OGS. https://online.ogs.ny.gov/purchase/spg/pdfdocs/3870022962ContractorInfo.pdf (accessed July 14, 2023).
[10] Atmospheric Solids Analysis Probe (ASAP) | Waters.
https://www.waters.com/nextgen/us/en/services/instrument-services/instrument-upgrades/mass-spectrometry-ms-upgrades/atmospheric-solids-analysis-probe.html (accessed July 14, 2023).
[11] ASAP® Probe, (n.d.). https://www.ionsense.com/Products/ASAP_Probe (accessed July 14, 2023).
[12] C. McEwen, S. Gutteridge, Analysis of the Inhibition of the Ergosterol Pathway in Fungi Using the Atmospheric Solids Analysis Probe (ASAP) Method, J. Am. Soc. Mass Spectrom. 18 (2007) 1274– 1278. https://doi.org/10.1016/j.jasms.2007.03.032.
[13] ASAP Atmospheric Solids Analysis Probe - Advion X Interchim, Advion. https://www.advion.com/products/asap/ (accessed July 15, 2023).
[14] J.M.C. Shaffer, L.-A. Giddings, R.M. Samples, J.A. Mikucki, Genomic and phenotypic characterization of a red-pigmented strain of Massilia frigida isolated from an Antarctic microbial mat, Front. Microbiol. 14 (2023). https://www.frontiersin.org/articles/10.3389/fmicb.2023.1156033 (accessed July 15, 2023).
[15] D. Vijay, N.S. Alshamsi, Z. Moussa, M.K. Akhtar, Extraction of the Anticancer and Antimicrobial Agent, Prodigiosin, from Vibrio gazogenes PB1 and Its Identification by 1D and 2D NMR, Molecules. 27 (2022) 6030. https://doi.org/10.3390/molecules27186030.
[16] B. Zakeri, G.D. Wright, Chemical biology of tetracycline antibioticsThis paper is one of a selection of papers published in this Special Issue, entitled CSBMCB — Systems and Chemical Biology, and has undergone the Journal’s usual peer review process., Biochem. Cell Biol. 86 (2008) 124–136. https://doi.org/10.1139/O08-002.
[17] A.E. Asagbra, A.I. Sanni, O.B. Oyewole, Solid-state fermentation production of tetracycline by Streptomyces strains using some agricultural wastes as substrate, World J. Microbiol. Biotechnol. 21 (2005) 107–114. https://doi.org/10.1007/s11274-004-2778-z.
[18] M. Beaumesnil, A.L. Mendes Siqueira, M. Hubert-Roux, C. Loutelier-Bourhis, C. Afonso, A. Racaud,
Y. Bai, High-performance thin-layer chromatography with atmospheric solids analysis probe mass spectrometry for analysis of gasoline polymeric additives, Rapid Commun. Mass Spectrom. 34 (2020) e8755. https://doi.org/10.1002/rcm.8755.
[19] W. Zhao, R. Jiang, W. Guo, C. Guo, S. Li, J. Wang, S. Wang, Y. Li, Screening and Analysis of Multiclass Veterinary Drug Residues in Animal Source Foods using UPLC-Q-Exactive Orbitrap/MS, Bull. Environ. Contam. Toxicol. 107 (2021) 228–238. https://doi.org/10.1007/s00128-021-03273-w.
[20] Y. Huang, Y. Hu, E.M. Yuill, A.S. Marriott, J. Chadwick, J. Li, J. Zang, S.A. Miller, Circumventing glass vial and diluent effects on solution stability of small molecule analytes during analytical method development and validation, J. Pharm. Biomed. Anal. 213 (2022) 114676. https://doi.org/10.1016/j.jpba.2022.114676.
[21] L.-A. Giddings, D.J. Newman, Bioactive Compounds from Extremophiles, in: L.-A. Giddings, D.J. Newman (Eds.), Bioactive Compounds from Extremophiles: Genomic Studies, Biosynthetic Gene Clusters, and New Dereplication Methods, Springer International Publishing, Cham, 2015: pp. 1–47. https://doi.org/10.1007/978-3-319-14836-6_1.
[22] L.-A. Giddings, D.J. Newman, Bioactive Compounds from Extremophiles, in: L.-A. Giddings, D.J. Newman (Eds.), Bioactive Compounds from Terrestrial Extremophiles., Springer International Publishing, Cham, 2015: pp. 1–47. https://doi.org/10.1007/978-3-319-13260-0

[23] L.-A. Giddings, D.J. Newman, Bioactive Compounds from Extremophiles, in: L.-A. Giddings, D.J. Newman (Eds.), Bioactive Compounds from Marine Extremophiles, Springer International Publishing, Cham, 2015: pp. 1–47. https://doi.org/10.1007/978-3-319-14361-3.
[24] A. Ahmad Dar, P. l. Sangwan, A. Kumar, Chromatography: An important tool for drug discovery, J. Sep. Sci. 43 (2020) 105–119. https://doi.org/10.1002/jssc.201900656.
[25] J. Tillner, V. Wu, E.A. Jones, S.D. Pringle, T. Karancsi, A. Dannhorn, K. Veselkov, J.S. McKenzie,
Z. Takats, Faster, More Reproducible DESI-MS for Biological Tissue Imaging, J. Am. Soc. Mass Spectrom. 28 (2017) 2090–2098. https://doi.org/10.1007/s13361-017-1714-z.
[26] N. Na, M. Zhao, S. Zhang, C. Yang, X. Zhang, Development of a Dielectric Barrier Discharge Ion Source for Ambient Mass Spectrometry, J. Am. Soc. Mass Spectrom. 18 (2007) 1859–1862. https://doi.org/10.1016/j.jasms.2007.07.027.
[27] S. Martínez-Jarquín, A. Moreno-Pedraza, H. Guillén-Alonso, R. Winkler, Template for 3D Printing a Low-Temperature Plasma Probe, Anal. Chem. 88 (2016) 6976–6980. https://doi.org/10.1021/acs.analchem.6b01019.

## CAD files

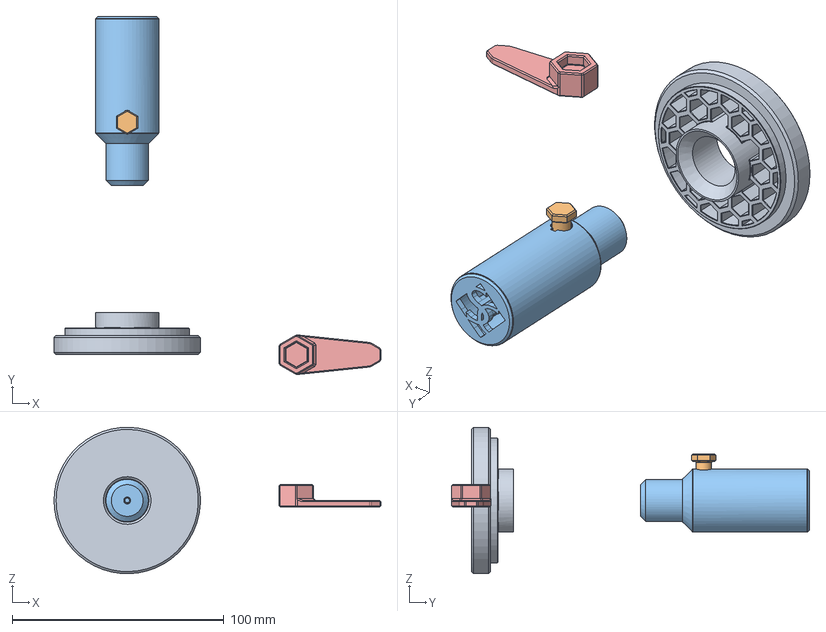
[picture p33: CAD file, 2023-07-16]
CAD/OpenASAP_IonMax_V1.step
154.6 x 169.3 x 69.2 mm
Port
Button
Probe_body
Spacer
Wrench

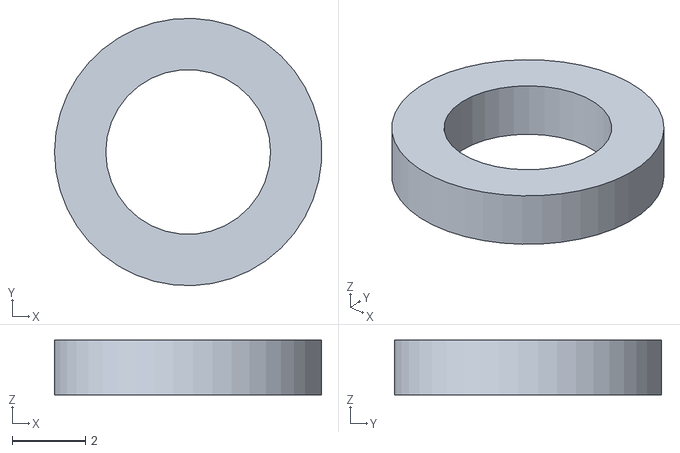
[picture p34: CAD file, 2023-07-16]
STL/spacer.stl
7.29 x 7.30 x 1.50

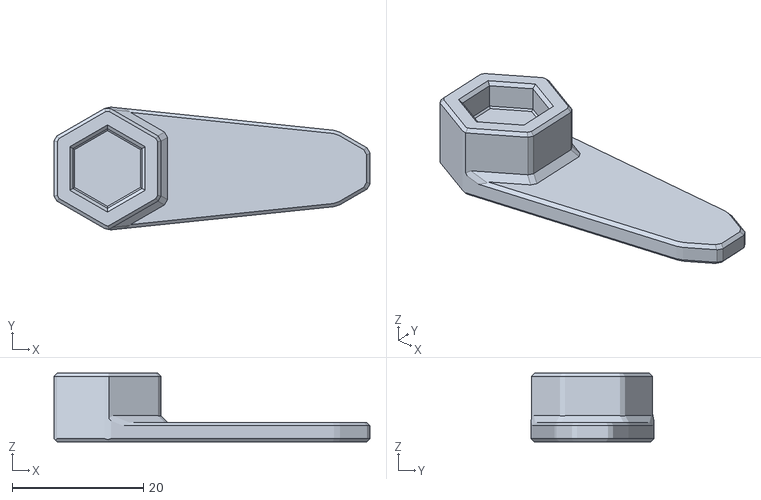
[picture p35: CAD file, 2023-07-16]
STL/wrench.stl
48.1 x 18.7 x 10.5

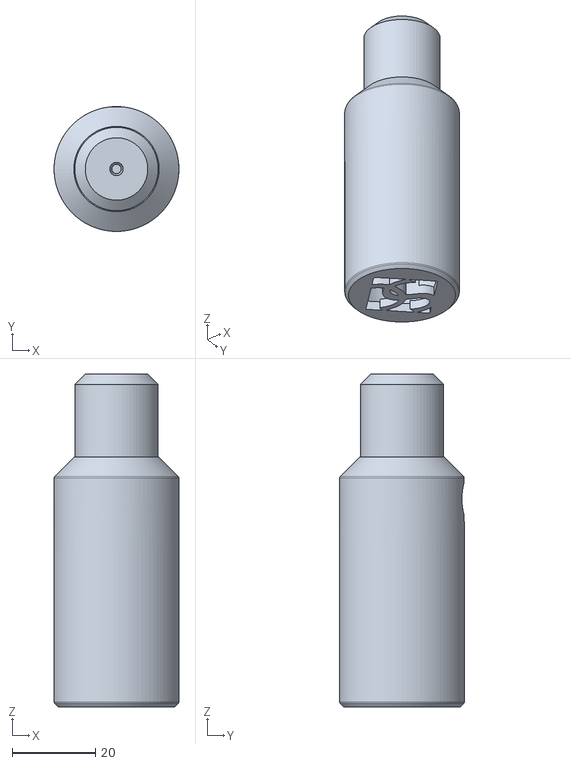
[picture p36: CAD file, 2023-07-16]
STL/probe_body.stl
30.0 x 30.0 x 80.0

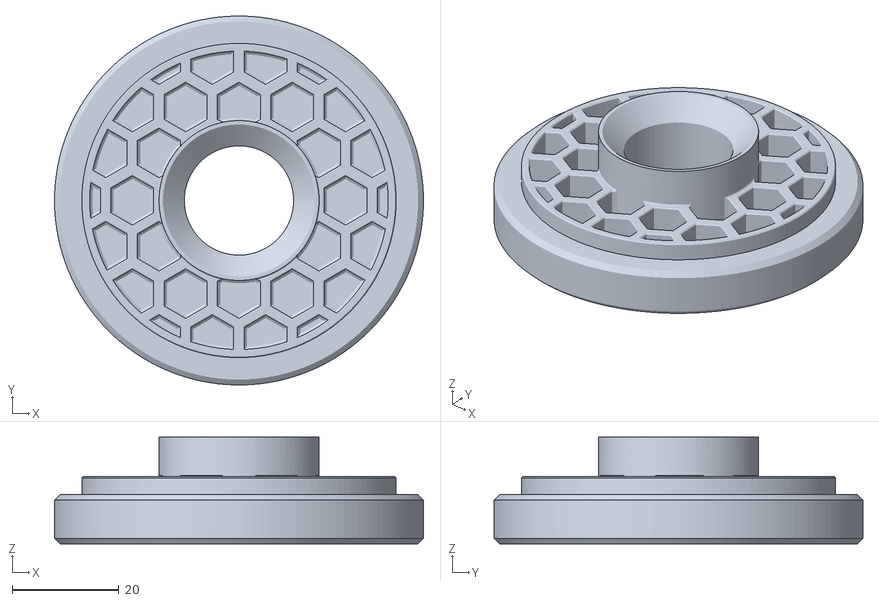
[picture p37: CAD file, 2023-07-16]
STL/port.stl
69.2 x 69.2 x 20.0

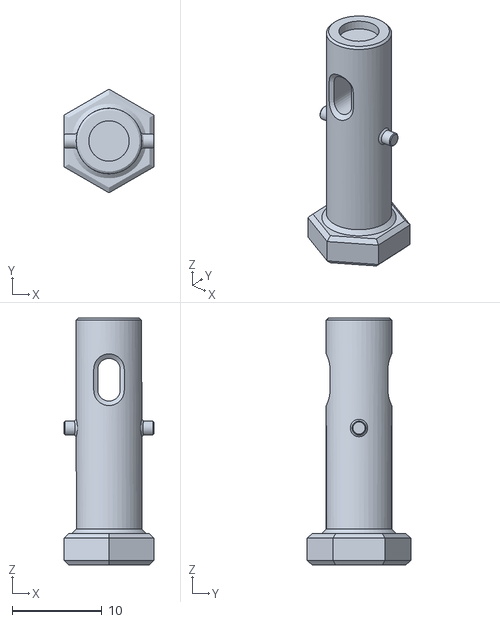
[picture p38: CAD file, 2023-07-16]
STL/button.stl
10.0 x 11.5 x 27.5
